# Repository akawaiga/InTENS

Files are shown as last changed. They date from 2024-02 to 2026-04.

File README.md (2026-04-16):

# InTENS project

# Overview
The InTENS is a high-frequency and high-intensity nerve stimulation
treatment for pain management. This project builds on prior research
from Boston Univesity's EDF and Bridge BUilders program, guided by a
physician, and is supplemented by phantom model testing and a new
electrode design.

# Features
*   single-channel system for compactness
*   delivers sine waves instead of commercial TENS pulse for user comfort
*   capable of delivering frequecnies up of atleast 1kHz
*   capable of delivering high-intensity waves of up to 140 Vpp

# Changes required to the board before use:

*   Solder a wire between pins 1 and 6 of U1 (best done on the bottom side)
This connects DAC reference to 5V
*   Solder a wire between J4 pin 3 and J2 pin 5
*   Solder a wire between J4 pin 4 and J2 pin 7
This connects the SPI data and clock to the right Arduino pins
*   addd a 100kohm resistor to R5 as 2mA is the reccommended ouptut current (for saftey)(ArduinoSheild PCB) 
*   addd a 100kohm resistor to C4 and C6 to reduce load on DC DC conversrters so both can function at same time (Battery PCB) 
*   heat sink reccommended on the 5V regulator (U1 on BatteryPCB) 

# User Interface 
Installation of Arduino IDE and Packages

* IDE download - https://www.arduino.cc/en/software
* Pathway to DAC MCP Package - https://github.com/akawaiga/InTENS/tree/main/Arduino 

Setup

*  Start Arduino IDE and connect the InTens device to the laptop. Ensure the correct board and output port are selected within the IDE. 
*  Ensure the DAC MCP library is downloaded from the GitHub repository
*  Set output baud rate to 11500
*  Upload the code to the Arduino and turn on both switches

Controlling Frequency and Amplitude

*   The initial frequency can be set using the freq variable. 
*   The initial amplitude can be set using the desiredAmplitude variable. 
*   The increment for the frequency can be set by changing the integer
  value in code line “freq+=10” and “freq-=10”.
*   The increment for the amplitude can be set by changing the integer
  value in code line “desiredAmplitude+=10” and
  “desiredAmplitude-=10”.
*   The frequency can be increased by entering “+” in the Arduino IDE.
*   The frequency can be decreased by entering “-” in the Arduino IDE.
*   The amplitude can be increased by entering “A” in the Arduino IDE. 
*   The amplitude can be decreased by entering “a” in the Arduino IDE. 

Note: 

You can compound your increments by adding multiple inputs at
once. For example: “+++++” or “AAAA”. Avoid combining inputs such as
“AaA”.

The code currently does not support decimal point increments (float),
please use integers such as “1” or “25”.

# Conclusion
Though with 2 PCBs we have acheived the orginal goal of creating a
TENS device capcable of creating a sine wave, >1kHz frequecny, and
140Vpp amplitude, we recommend the following updates to the next
iteration of the device:

*   Shaft Encoder:incorporate a knob to manually control frequency and
  amplitude rather than through the IDE. This has been done in
  previous versions of the device (2021-22)
*   LCD Display:incorporate LCD display to show output frequency and
  amplitude and various parameter changes when changing parameters
  using the knob.
*   Float type increments: currently the code uses type int for the
  amplitude and frequency variables, update this to type float to
  allow decimal increments.
*   Safety: consult with electrical engineers to build in further safety
  features to ensure the device does not provide unwanted currents to
  the patient.
*   Finger Clamp: update the finger clamp design to include jaws
  (example a claw hair clip) so it can accommodate smaller patient
  anatomies.
*   Phantom Testing: continue developing a phantom model for the finger
  to demonstrate safety and efficacy.

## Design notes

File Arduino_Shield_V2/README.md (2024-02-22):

# Design review 2/22/24

**Schematic / Overall**

* Why the change to the TSSOP package for the LTC6090?.  The SO-8
  package is much easier to solder and in stock.
* Missing HV power supplies on the LTC6090.  You need to be able to
  supply external power to this for testing at voltages above 5V.
  Suggest to add a 3 pin connector with +HV, GND, -HV which are
  connected to the V+, GND, V- on the LTC6090
* The chips are missing bypass capacitors.  Please read over the
  datahsheets for recommendations.  These are capacitors to GND on
  each power supply to a chip (so total of 3 minimum, Vdd the MCP4921
  and two on V+ and V- of the LTC6090)  
* Mounting holes should be on schematic
* Name symbols consistently:  you have U1 and IC1 where you should
  have U1 and U2.
* Don't interconnect the two SDA and SCL pins on the Arduino.

**PCB Layout**

The layout looks nice and neat, but there are quite a few issues which
should be addressed to ensure good performance:

* There must be an overall GND plane.  This is most easily done by
  converting the design to 4 layers and using an inner layer for this.
* The bypass capacitors mentioned above need to be placed near the
  chips.
* The datasheet for the LTC6090 (did you read it?) specifically
  reccomends surface-mount components.  I highly recommend switching
  all the passives (R, C) to surface mount.  An 0805 or 1206 size is
  quite large and easy to use.  I can help you with soldering them.

The wiring seems a bit random... did you use the autoroute feature?
Never do that.

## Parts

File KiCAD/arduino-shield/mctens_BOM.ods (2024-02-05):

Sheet: mctens
Please order for two boards plus 1 spare of each IC and round up on the passives.
Reference | Qty/Board | Value | Footprint | CatNo | Vendor | QQ | Project
BT1 BT2 | 2 | Battery_Holder |  | 36-2478-ND | DigiKey |  | MULTI-TEMS
C3 | 1 | 1uF | Capacitor_THT:C_Disc_D3.4mm_W2.1mm_P2.50mm | 399-14394-1-ND | DigiKey |  | MULTI-TEMS
C1 C2 C4 C5 C6 C11 | 6 | 0.1uF | Capacitor_THT:C_Disc_D3.4mm_W2.1mm_P2.50mm | 399-9859-2-ND | DigiKey |  | MULTI-TEMS
C7 C8 C9 C10 | 4 | OMIT | Capacitor_THT:C_Disc_D3.4mm_W2.1mm_P2.50mm | OMIT
D1 D2 D3 D4 | 4 | 1N4005 | Diode_THT:D_DO-41_SOD81_P10.16mm_Horizontal | 1N4007-TPMSCT-ND | DigiKey |  | MULTI-TEMS
D5 D6 | 2 | LED | LED_THT:LED_D3.0mm | 1497-XLMDK65D-ND | DigiKey |  | MULTI-TEMS
H1 H2 H3 H4 | 4 | MountingHole | MountingHole:MountingHole_4.3mm_M4 | OMIT
J1 | 1 | Conn_01x02 | Connector_Molex:Molex_Mini-Fit_Jr_5566-02A_2x01_P4.20mm_Vertical | WM23820-ND | DigiKey |  | MULTI-TEMS
J2 J3 J4 J5 | 4 | CONN | Connector_PinHeader_2.54mm:PinHeader_1x02_P2.54mm_Vertical | S1011EC-02-ND | DigiKey |  | MULTI-TEMS
J6 | 1 | Conn_01x16 | Connector_PinHeader_2.54mm:PinHeader_1x16_P2.54mm_Vertical | 2057-PH1-16-UA-ND | DigiKey |  | MULTI-TEMS
N1 | 1 | Enclosure_1591DSBK |  | HM105-ND | DigiKey |  | MULTI-TEMS
Q1 Q2 Q3 Q4 | 4 | FQP19N20C | Package_TO_SOT_THT:TO-220-3_Vertical | FQP19N20C-ND | DigiKey |  | MULTI-TEMS
R12 | 1 | 1k | Resistor_THT:R_Axial_DIN0207_L6.3mm_D2.5mm_P10.16mm_Horizontal | Generic 1k ohm 1/4W | DigiKey |  | MULTI-TEMS
R10 R13 R14 R15 | 4 | 10k | Resistor_THT:R_Axial_DIN0207_L6.3mm_D2.5mm_P10.16mm_Horizontal | Generic 10k ohm 1/4W | DigiKey |  | MULTI-TEMS
R11 R16 R17 | 3 | 2k | Resistor_THT:R_Axial_DIN0207_L6.3mm_D2.5mm_P10.16mm_Horizontal | Generic 2k ohm 1/4W | DigiKey |  | MULTI-TEMS
R1 R2 R3 R6 R7 | 5 | 100 | Resistor_THT:R_Axial_DIN0207_L6.3mm_D2.5mm_P10.16mm_Horizontal | Generic 100 ohm 1/4W | DigiKey |  | MULTI-TEMS
R4 R5 R8 R9 | 4 | 8R2 2W | Resistor_THT:R_Axial_DIN0414_L11.9mm_D4.5mm_P20.32mm_Horizontal | 8.2 ohm 2W | DigiKey |  | MULTI-TEMS
RV1 | 1 | 5K | Potentiometer_THT:Potentiometer_Bourns_3266P_Horizontal | 3266P-1-502LF-ND | DigiKey |  | MULTI-TEMS
SW1 | 1 | SW_SPST | arduino-shield:SW-A11AB | 360-3868-ND | DigiKey |  | MULTI-TEMS
SW2 | 1 | COM-15140 | arduino-shield:rotary-RG | OMIT
T1 T2 T3 T4 | 4 | Transformer_1P_1S | arduino-shield:42TL-transformer | OMIT - customer
U2 | 1 | 12V_3.3V_DC | Package_TO_SOT_THT:TO-220-3_Vertical | 1951-TSR1.5-2433E-ND | DigiKey |  | MULTI-TEMS
U3 | 1 | LM358 | Package_DIP:DIP-8_W7.62mm_Socket_LongPads | LM2904NNS/NOPB-ND | DigiKey |  | MULTI-TEMS
U4 | 1 | MAX4678 | Package_DIP:DIP-16_W7.62mm_Socket_LongPads | MAX4678EPE+-ND | DigiKey |  | MULTI-TEMS
U5 | 1 | ARDUINO_PRO_MINI | arduino-shield:MODULE_ARDUINO_PRO_MINI
XX1 | 4 | 2 Pin Housing |  | WM2800 | DigiKey | 4 | MULTI-TEMS
XX2 | 8 | Crimp Pins |  | WM2513 | DigiKey | 8 | MULTI-TEMS
XX3 | 4 | 3.5 mm jack |  | 839-1410-ND | DigiKey | 4 | MULTI-TEMS
XX4 | 4 | 3.5 mm cable |  | 839-1033-ND | DigiKey | 4 | MULTI-TEMS
XX5 | 4 | 16 pin socket |  | 929850-01-16-ND | DigiKey | 4 | MULTI-TEMS

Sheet: EDF stock
Qty
20 | Breakaway header | 3M11928-ND | DigiKey | EDF Stock
20 | Breakaway socket | 929850-01-36-ND | DigiKey | EDF Stock
10 | Breakaway header long pins | SAM1123-32-ND | DigiKey | EDF Stock
10 | Breakaway header two row | S2011EC-40-ND | DigiKey | EDF Stock

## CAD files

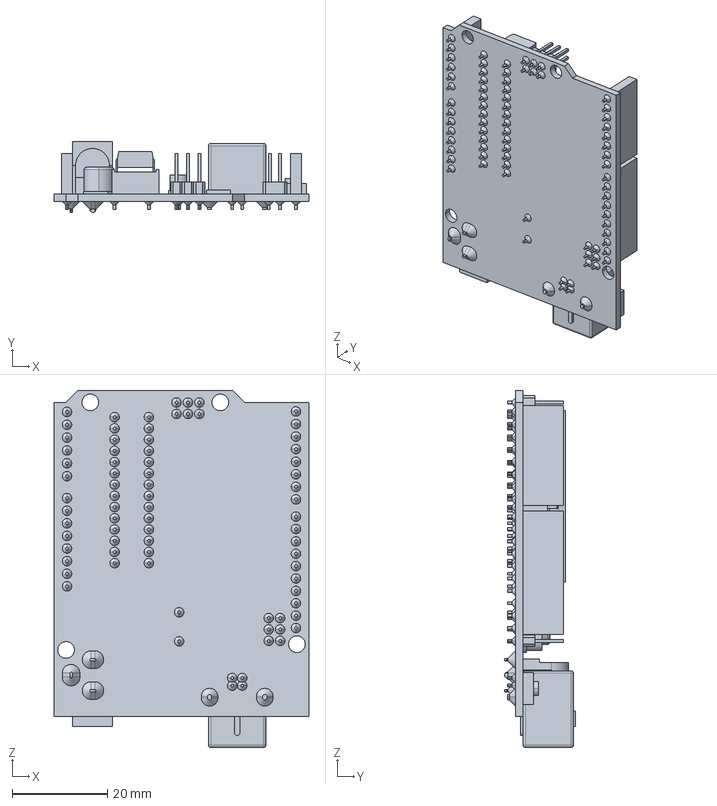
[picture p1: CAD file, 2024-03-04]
Arduino_Shield_V2/Arduino-UNO.stp
53.5 x 14.9 x 75.0 mm

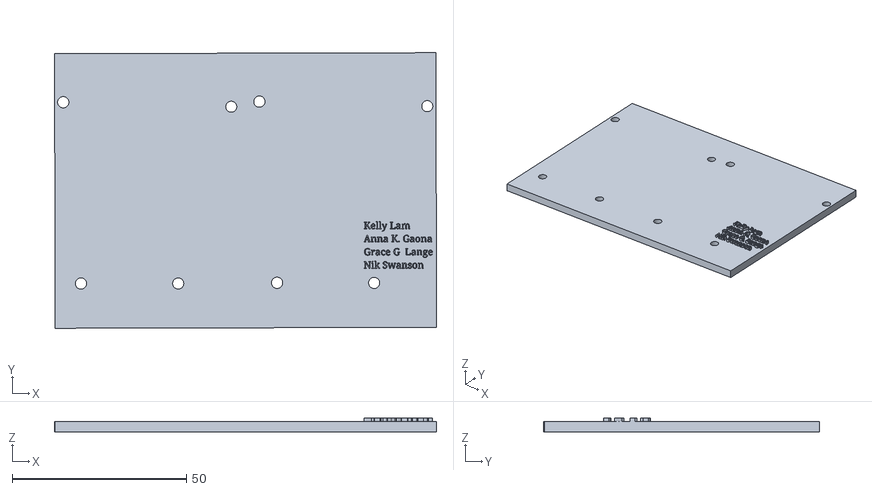
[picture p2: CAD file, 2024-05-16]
CAD Designs/layer.stl
109.8 x 79.2 x 4.00

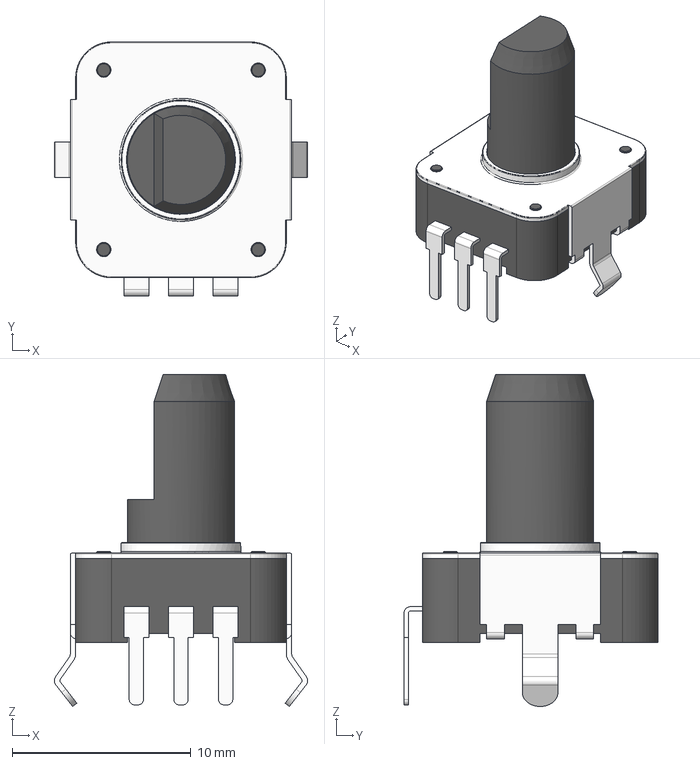
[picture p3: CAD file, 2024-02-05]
KiCAD/arduino-shield/3D/EC12 Encoder 10mm 3pin.stp
14.2 x 14.2 x 18.6 mm

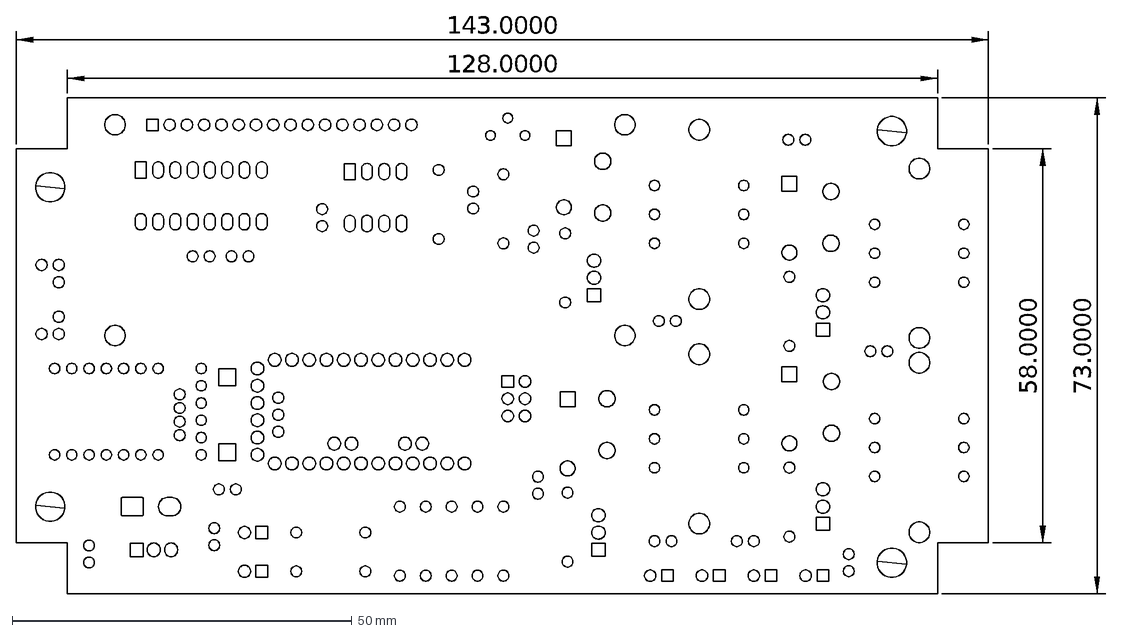
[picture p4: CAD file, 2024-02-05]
KiCAD/arduino-shield/DXF/mctens-Edge_Cuts.dxf
128.0000
143.0000
58.0000
73.0000

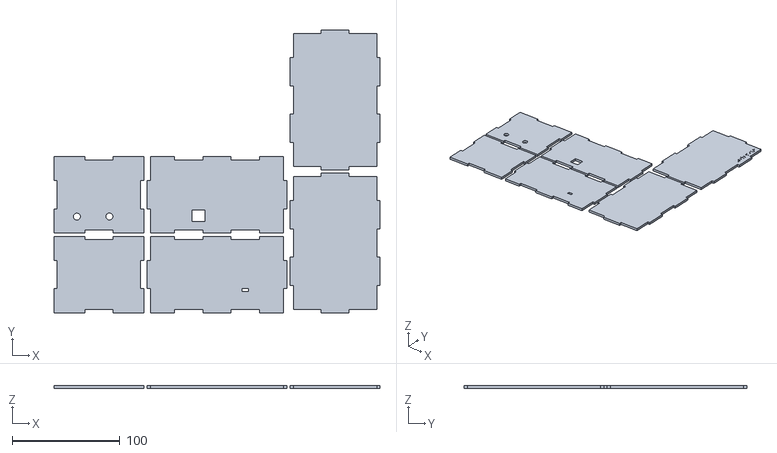
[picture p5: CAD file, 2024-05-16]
CAD Designs/makercase.stl
302.7 x 262.4 x 3.20

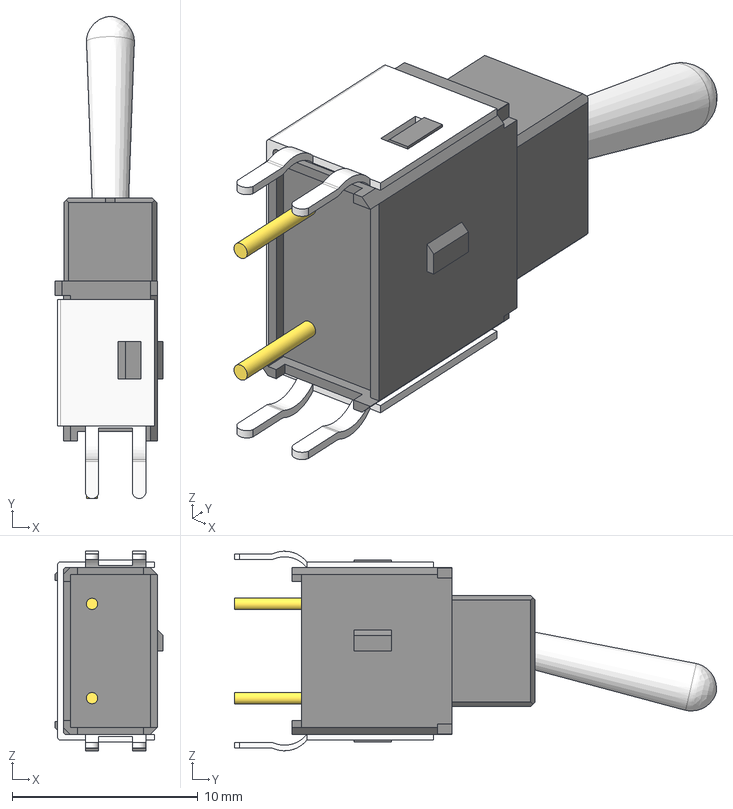
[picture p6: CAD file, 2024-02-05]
KiCAD/arduino-shield/3D/A11AB.stp
5.84 x 26.0 x 10.8 mm
_A1-toggle-body
_A11B-toggle-terminals
_A1B-toggle-bracket_str
_AA-toggle-toggle

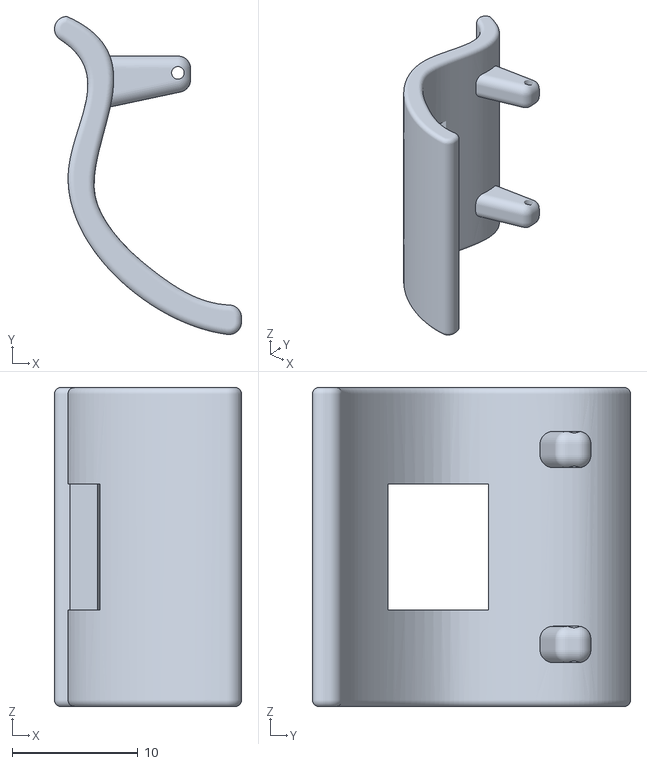
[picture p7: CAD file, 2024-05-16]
CAD Designs/halfclamplargedistance.STL
14.9 x 25.3 x 25.4

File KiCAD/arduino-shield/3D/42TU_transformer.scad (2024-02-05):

// 42TU transformer

dy = .1675;
dx = .517;

cx = 0.72;
cy = 0.98;
cz = 0.74;

module trans() {
  // body
  color("grey")
    translate( [cx/3, 0, 0])
      cube( [cx/3, cy, cz]);
  color("#e0e0e0") {
      translate( [0, cy/5, cz/8])  cube( [cx, cy*3/5, 0.063]);
      translate( [0, cy/5, cz*6/8])  cube( [cx, cy*3/5, 0.063]);
  }
  color("#ffffe0") {
    translate( [cx/8, cy/5, cz/8])  cube( [cx*3/4, cy*3/5, cz*5/8]);
  }

  // wires
  translate( [0.1, 0.323, -.197]) {
    for( ix=[0:1]) {
      for( iy=[0:2]) {
	translate( [ix*dx, iy*dy, 0])
	  cylinder( d=.02, h=.3);
      }
    }
  }

  // tabs
  color("#e0e0e0") {
    translate( [cx/2-.05, 0, -0.2])
      cube( [.1, .03, .2]);
    translate( [cx/2-.05, cy-.03, -0.2])
      cube( [.1, .03, .2]);
  }
}

trans();

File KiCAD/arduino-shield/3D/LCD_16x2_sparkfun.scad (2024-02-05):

module lcd() {

  // PCB with mounting holes
  difference() {
    color("#006020")  cube([80,36,1.6]);
    translate( [0, 0, -0.1]) {
      $fn = 24;
      translate( [2.5, 2.5, 0])  cylinder( d=2.5, h=1.8);
      translate( [2.5, 36-2.5, 0])  cylinder( d=2.5, h=1.8);
      translate( [80-2.5, 2.5, 0])  cylinder( d=2.5, h=1.8);
      translate( [80-2.5, 36-2.5, 0])  cylinder( d=2.5, h=1.8);
    }
  }
  // display body
  translate([4.35, 4.85, 3.2]) color("grey") cube([71.3, 26.3, 5.4]);
  // connector pins
  color("#FFFF00")
  translate( [8, 36-2.5, -5]) {
    $fn = 4;
    for( i=[0:15]) {
      translate( [i*2.54, 0, 0])
	cylinder( d=1.0,h=7);
    }
  }
}

lcd();


    

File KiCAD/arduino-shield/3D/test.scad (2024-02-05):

// PCB with mounting holes
difference() {
  color("#006020")  cube([80,36,1.6]);
  translate( [0, 0, -0.1]) {
    $fn = 24;
    translate( [2.5, 2.5, 0])  cylinder( d=2.5, h=1.8);
    translate( [2.5, 36-2.5, 0])  cylinder( d=2.5, h=1.8);
    translate( [80-2.5, 2.5, 0])  cylinder( d=2.5, h=1.8);
    translate( [80-2.5, 36-2.5, 0])  cylinder( d=2.5, h=1.8);
  }
}
// display body
translate([4.35, 4.85, 3.2]) color("grey") cube([71.3, 26.3, 5.4]);
// connector pins
translate( [8, 36-2.5, -5]) {
  for( i=[0:15]) {
    translate( [i*2.54, 0, 0])
    cylinder( d=1.0,h=7);
  }
}

    

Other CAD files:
KiCAD/arduino-shield/DXF/mctens-F_Mask.dxf

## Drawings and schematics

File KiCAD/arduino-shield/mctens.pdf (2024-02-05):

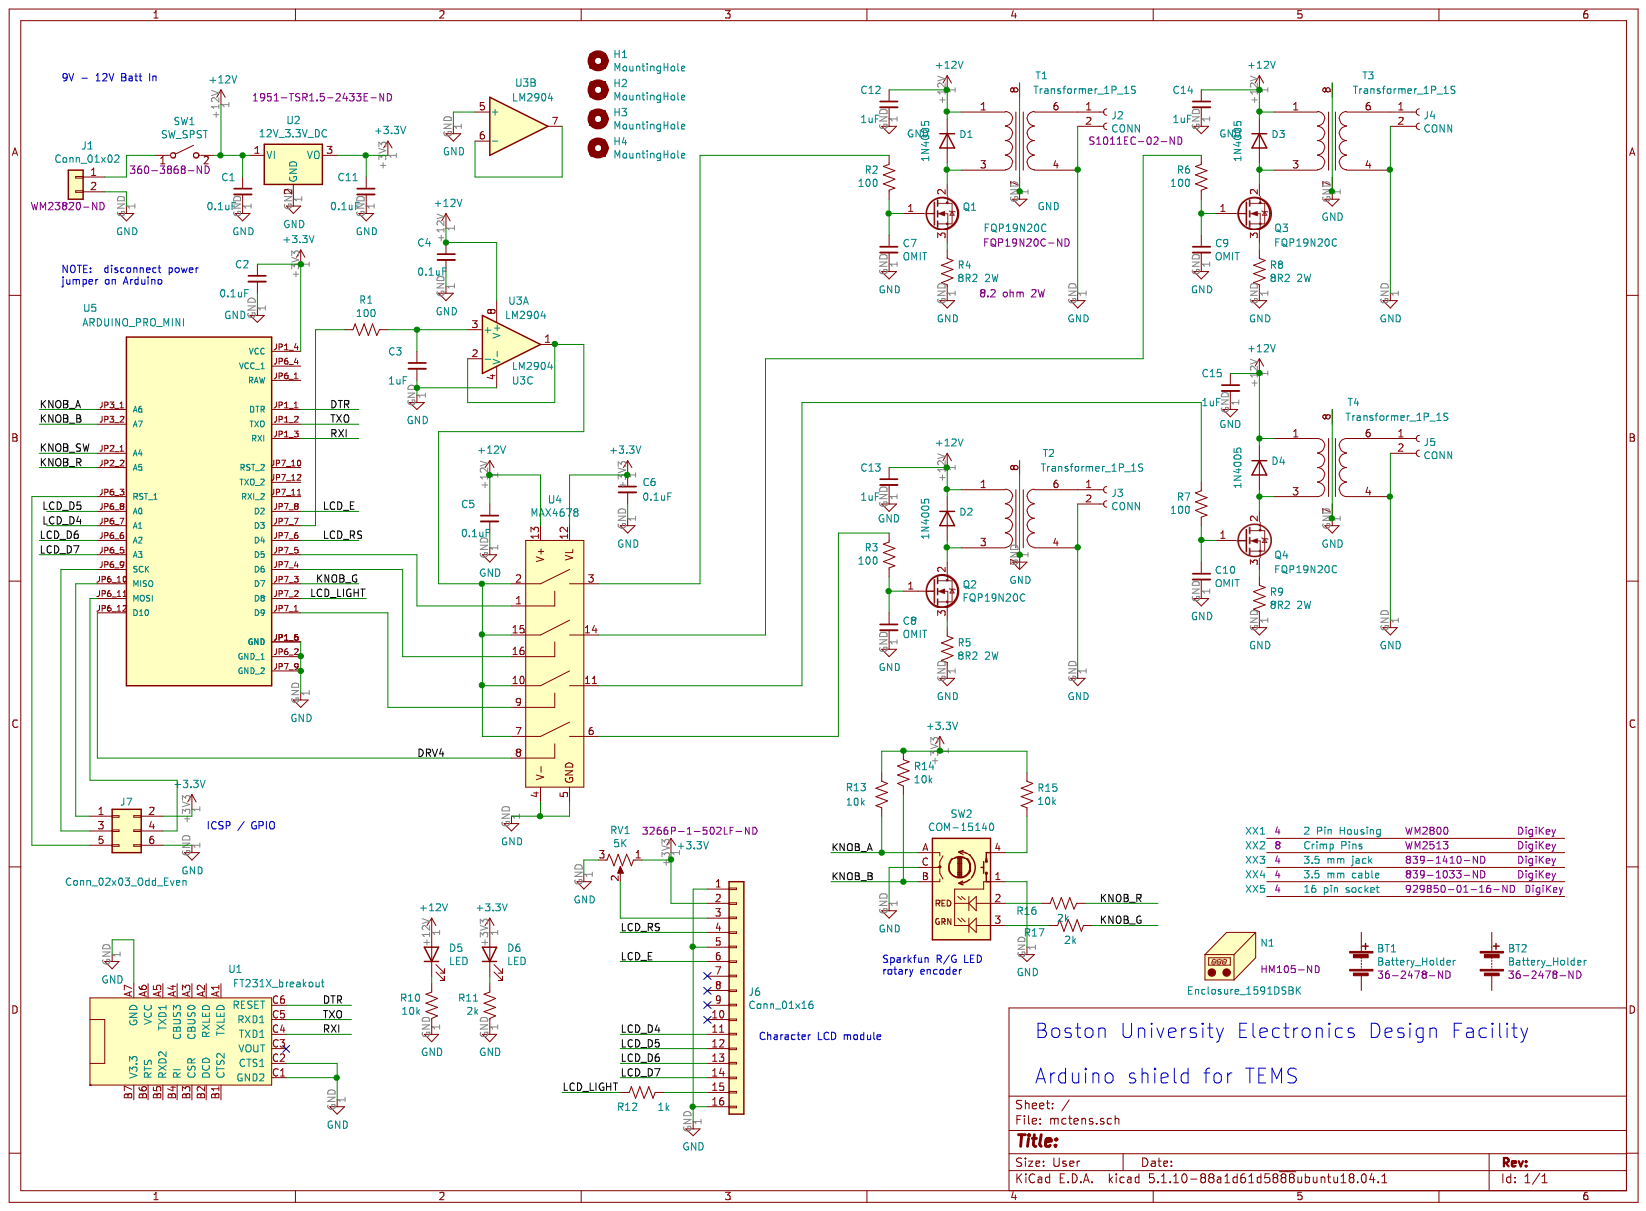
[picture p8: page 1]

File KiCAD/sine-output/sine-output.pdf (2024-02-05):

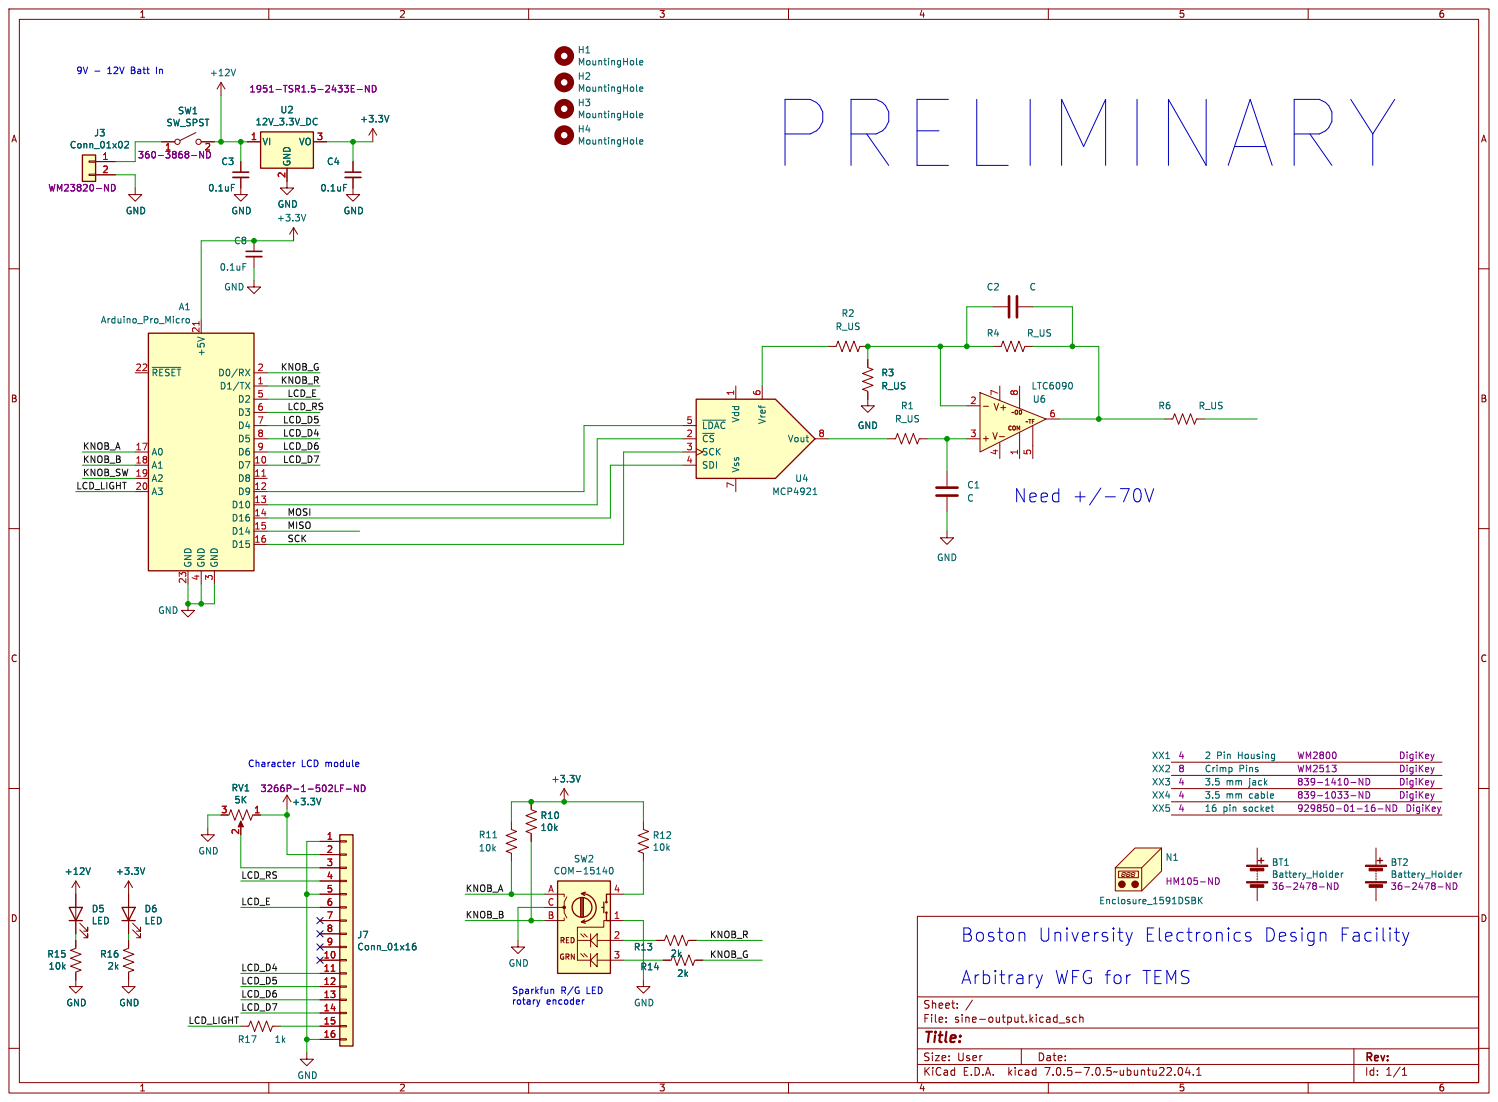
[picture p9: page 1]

1 ~{CS} 2 SCK 3 SDI 4 ~{LDAC} 5 Vref 6 Vss 7 Vout 8 U4 MCP4921 GND

Arbitrary WFG for TEMS

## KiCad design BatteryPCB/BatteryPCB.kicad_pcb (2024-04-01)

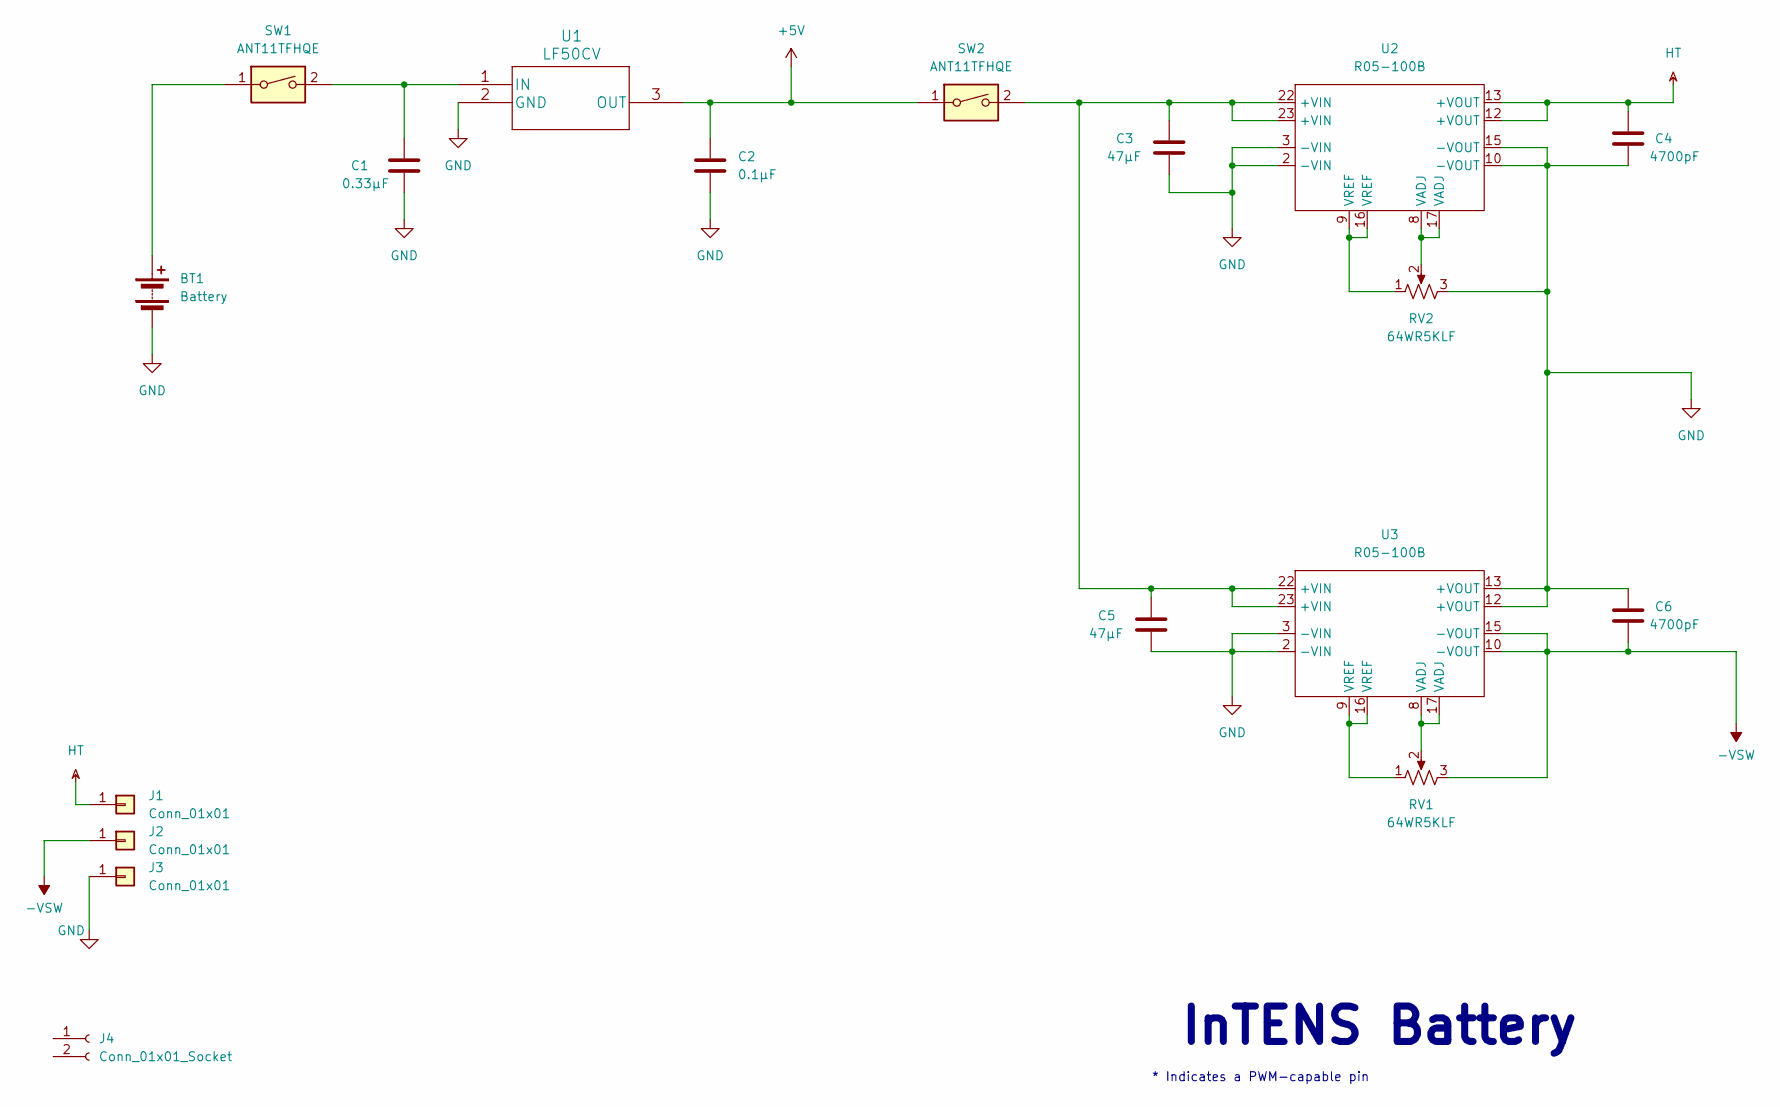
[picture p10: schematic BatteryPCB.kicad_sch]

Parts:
BT1: Battery; CON_39296028
C1: 0.33μF; C_Rect_L4.6mm_W2.0mm_P2.50mm_MKS02_FKP02
C2: 0.1μF; C_Rect_L4.6mm_W2.0mm_P2.50mm_MKS02_FKP02
C3, C5: 47μF; C_1206_3216Metric_Pad1.33x1.80mm_HandSolder
C4, C6: 4700pF; C_1206_3216Metric_Pad1.33x1.80mm_HandSolder
J1, J2, J3: Conn_01x01; Pin_D1.0mm_L10.0mm
J4: Conn_01x01_Socket; PinSocket_1x02_P2.54mm_Vertical
RV1, RV2: 64WR5KLF; RES3_64W_TTE
SW1, SW2: ANT11TFHQE; 100SP1T1_EWI
U1: LF50CV
U2, U3: R05-100B; DIP-24_W15.24mm

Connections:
+5V: C2.1, SW2.1, U1.3 (OUT)
-VSW: C6.1, J2.1, RV1.3, U3.10 (-VOUT), U3.15 (-VOUT)
GND: BT1.2 (-), C1.2, C2.2, C3.1, C4.1, C5.1, C6.2, J3.1, RV2.3, U1.2 (GND), U2.2 (-VIN), U2.3 (-VIN), U2.10 (-VOUT), U2.15 (-VOUT), U3.2 (-VIN), U3.3 (-VIN), U3.12 (+VOUT), U3.13 (+VOUT)
HT: C4.2, J1.1, U2.12 (+VOUT), U2.13 (+VOUT)
unnamed: BT1.1 (+), SW1.1
unnamed: C3.2, C5.2, SW2.2, U2.22 (+VIN), U2.23 (+VIN), U3.22 (+VIN), U3.23 (+VIN)
unnamed: RV1.1, U3.9 (VREF), U3.16 (VREF)
unnamed: RV1.2, U3.8 (VADJ), U3.17 (VADJ)
unnamed: RV2.1, U2.9 (VREF), U2.16 (VREF)
unnamed: RV2.2, U2.8 (VADJ), U2.17 (VADJ)
unnamed: C1.1, SW1.2, U1.1 (IN)

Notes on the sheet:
InTENS Battery
* Indicates a PWM-capable pin

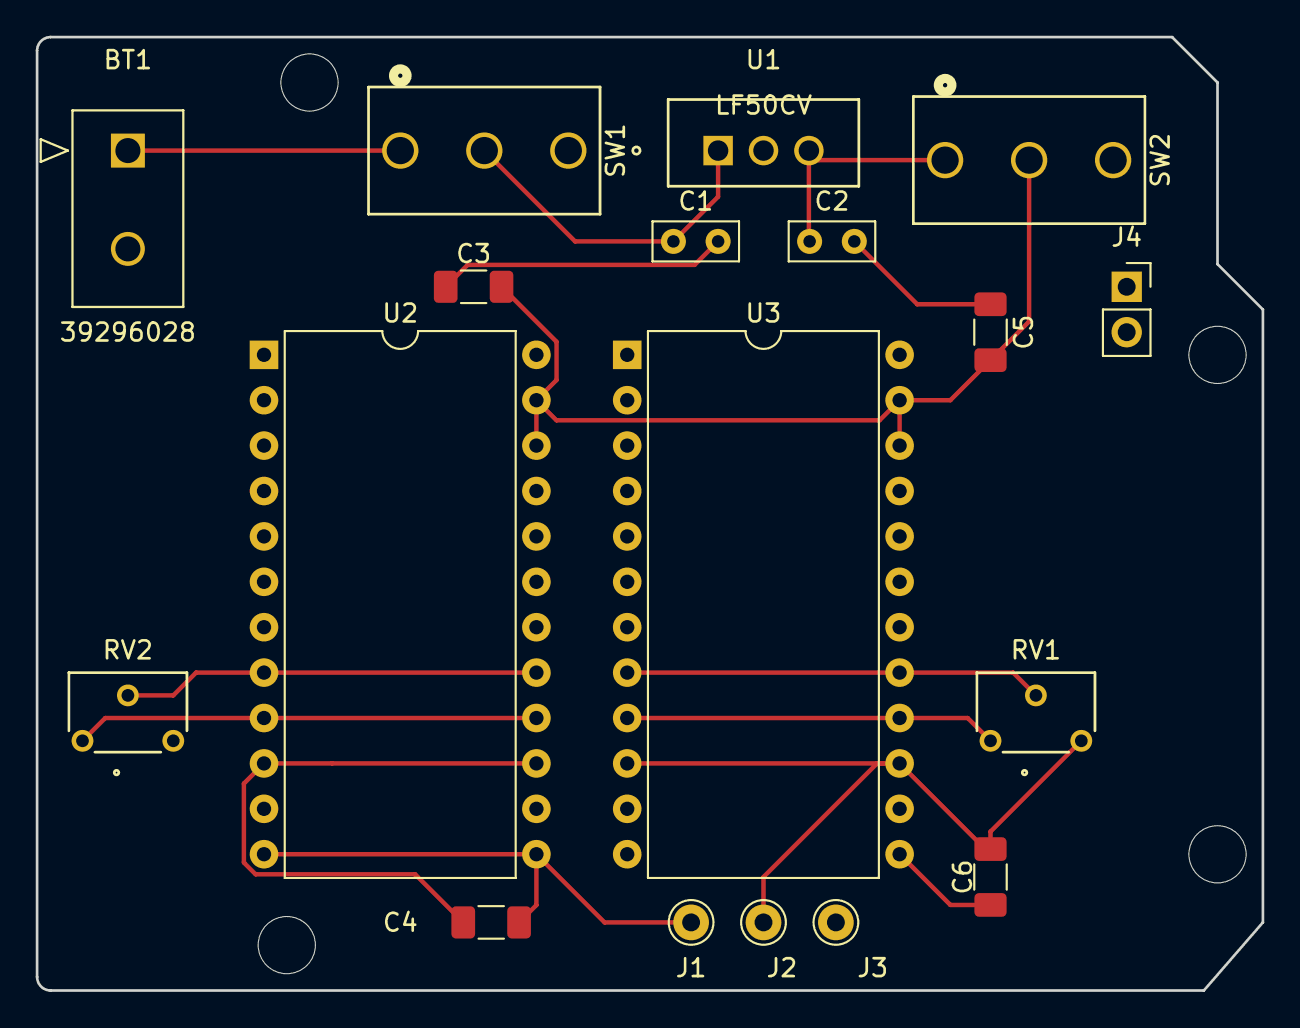
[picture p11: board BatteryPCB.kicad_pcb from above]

Board: 2 copper layers, 68.6 x 53.3 mm, 22 parts (0 on the bottom side), 11 nets.

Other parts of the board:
MH1, MH2, MH3, MH4: MountingHole_3.2mm

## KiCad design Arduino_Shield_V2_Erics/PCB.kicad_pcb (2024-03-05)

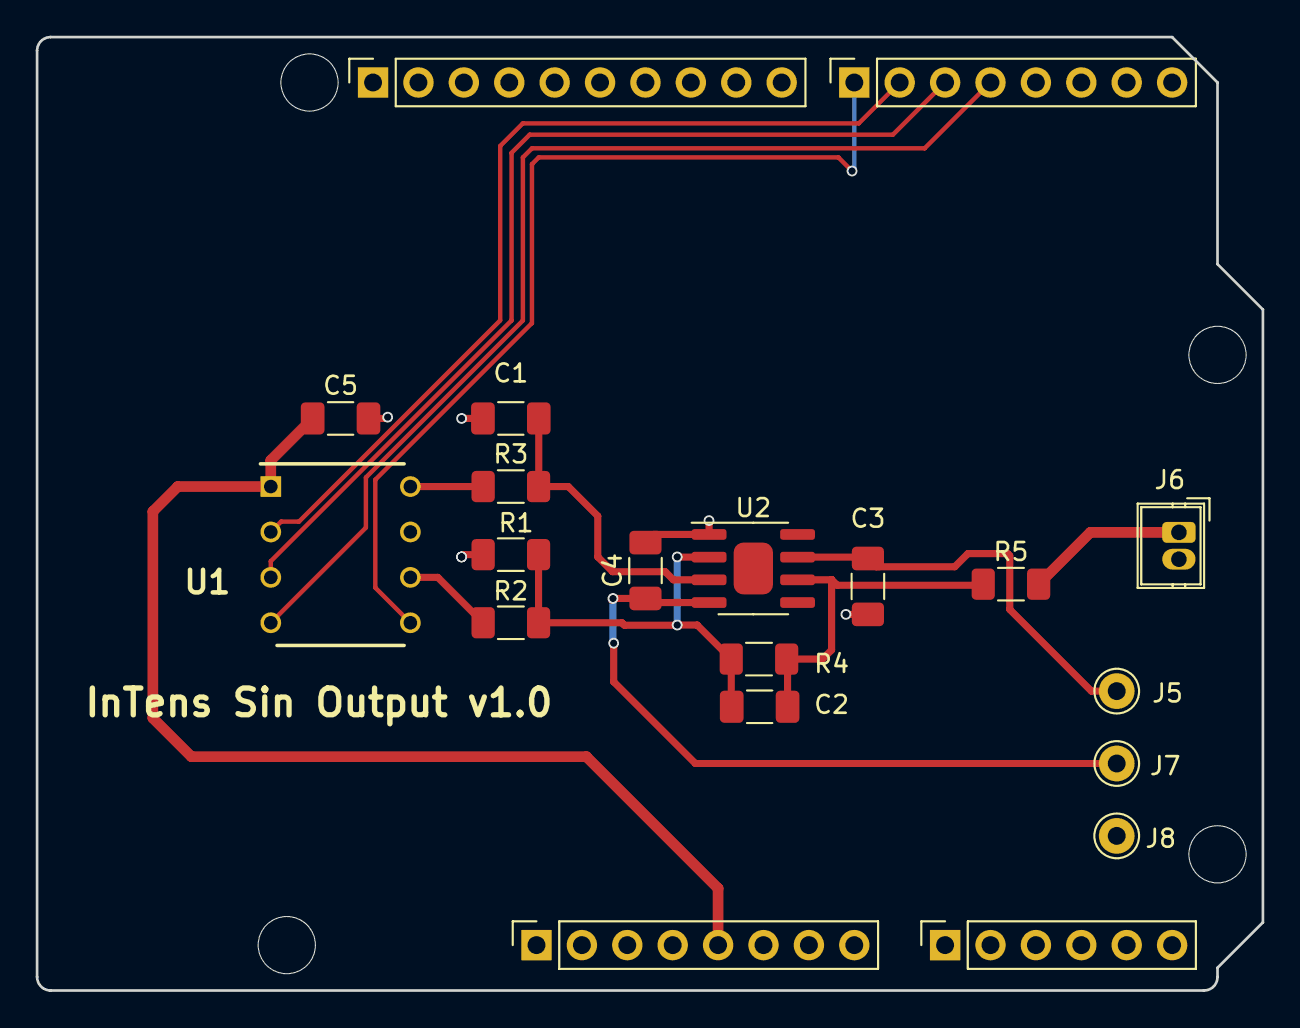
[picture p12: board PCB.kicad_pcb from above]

Board: 2 copper layers, 68.6 x 53.3 mm, 24 parts (0 on the bottom side), 15 nets.

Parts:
C1: 470pF; C_1206_3216Metric_Pad1.33x1.80mm_HandSolder
C2: 10pF; C_1206_3216Metric_Pad1.33x1.80mm_HandSolder
C3, C4: 0.1uF; C_1206_3216Metric_Pad1.33x1.80mm_HandSolder
C5: 0.1 uF; C_1206_3216Metric_Pad1.33x1.80mm_HandSolder
J1: Power; PinSocket_1x08_P2.54mm_Vertical
J2: Digital/PWM; PinSocket_1x10_P2.54mm_Vertical
J3: Analog; PinSocket_1x06_P2.54mm_Vertical
J4: Digital/PWM; PinSocket_1x08_P2.54mm_Vertical
J5, J7, J8: Conn_01x01; Pin_D1.0mm_L10.0mm
J6: Conn_01x01_Socket; Wuerth_WR-WTB_64800211622_1x02_P1.50mm_Vertical
MH1, MH2, MH3, MH4: MountingHole_3.2mm
R1: 16.2kΩ; R_1206_3216Metric_Pad1.30x1.75mm_HandSolder
R2: 16.9kΩ; R_1206_3216Metric_Pad1.30x1.75mm_HandSolder
R3: 10kΩ; R_1206_3216Metric_Pad1.30x1.75mm_HandSolder
R4: 453kΩ; R_1206_3216Metric_Pad1.30x1.75mm_HandSolder
R5: 40kΩ; R_1206_3216Metric_Pad1.30x1.75mm_HandSolder
U1: MCP4921; DIP781W56P254L950H533Q8N
U2: LTC6090; SOIC-8-1EP_3.9x4.9mm_P1.27mm_EP2.29x3mm

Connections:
+5V: C5.1, J1.5, U1.1 (Vdd)
-VSW: C4.1, J7.1, U2.4
/4: J4.4, U1.4 (SDI)
/7: J4.1, U1.5 (~LDAC)
/*5: J4.3, U1.3 (SCK)
/*6: J4.2, U1.2 (~CS)
GND: C1.2, C3.2, C4.2, C5.2, J1.6, J1.7, J2.4, J6.2, J8.1, R2.1, U1.7 (Vss), U2.1
HT: C3.1, J5.1, U2.7
unnamed: C1.1, R3.2, U2.3
unnamed: C2.1, R1.1, R2.2, R4.1, U2.2
unnamed: C2.2, R4.2, R5.1, U2.6
unnamed: J6.1, R5.2
unnamed: R3.1, U1.8 (Vout)
unnamed: R1.2, U1.6 (Vref)
unnamed: U2.5, U2.8

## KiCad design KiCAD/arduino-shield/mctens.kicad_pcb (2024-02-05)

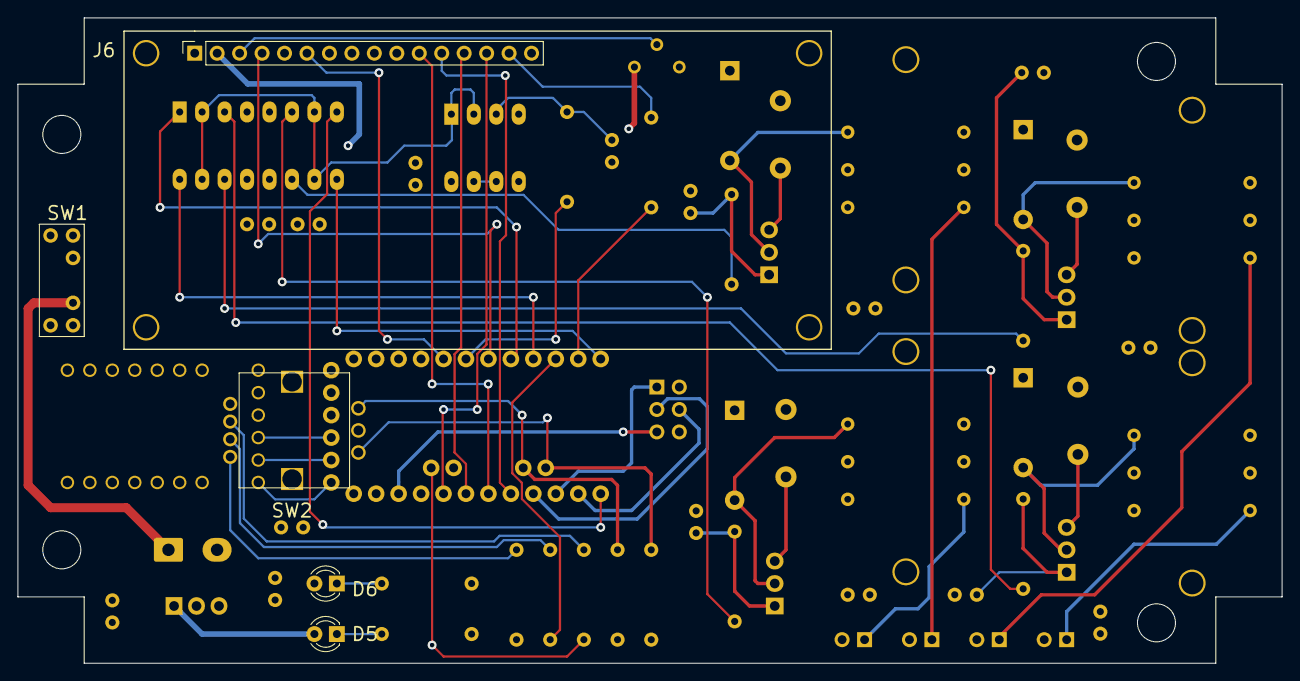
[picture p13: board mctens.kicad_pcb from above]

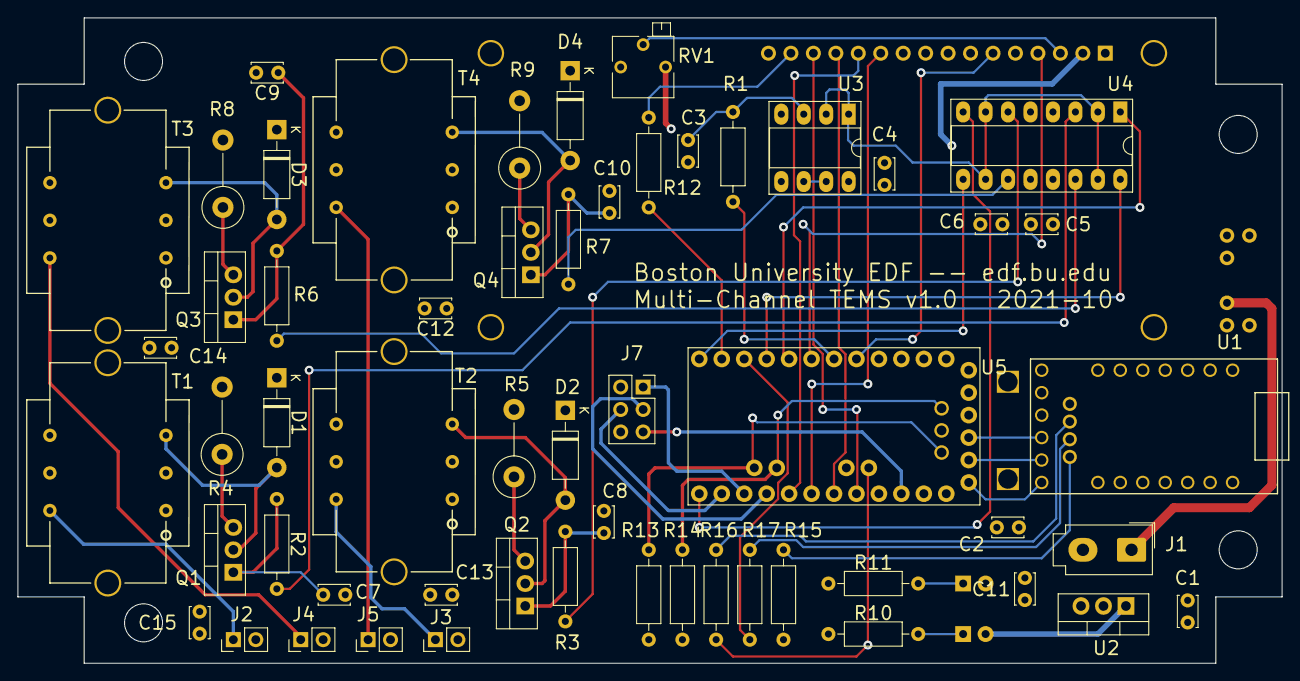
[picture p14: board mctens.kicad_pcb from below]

Board: 4 copper layers, 143.0 x 73.0 mm, 65 parts (56 on the bottom side), 57 nets.

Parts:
C1, C2, C4, C5, C6, C11: 0.1uF; C_Disc_D3.4mm_W2.1mm_P2.50mm
C3, C12, C13, C14, C15: 1uF; C_Disc_D3.4mm_W2.1mm_P2.50mm
C7, C8, C9, C10: OMIT; C_Disc_D3.4mm_W2.1mm_P2.50mm
D1, D2, D3, D4: 1N4005; D_DO-41_SOD81_P10.16mm_Horizontal
D5, D6: LED; LED_D3.0mm
H1, H2, H3, H4: MountingHole; MountingHole_4.3mm_M4
J1: Conn_01x02; Molex_Mini-Fit_Jr_5566-02A_2x01_P4.20mm_Vertical
J2, J3, J4, J5: CONN; PinHeader_1x02_P2.54mm_Vertical
J6: Conn_01x16; LCD_module_3D
J7: Conn_02x03_Odd_Even; PinSocket_2x03_P2.54mm_Vertical
Q1, Q2, Q3, Q4: FQP19N20C; TO-220-3_Vertical
R1, R2, R3, R6, R7: 100; R_Axial_DIN0207_L6.3mm_D2.5mm_P10.16mm_Horizontal
R4, R5, R8, R9: 8R2 2W; R_Axial_DIN0414_L11.9mm_D4.5mm_P7.62mm_Vertical
R10, R13, R14, R15: 10k; R_Axial_DIN0207_L6.3mm_D2.5mm_P10.16mm_Horizontal
R11, R16, R17: 2k; R_Axial_DIN0207_L6.3mm_D2.5mm_P10.16mm_Horizontal
R12: 1k; R_Axial_DIN0207_L6.3mm_D2.5mm_P10.16mm_Horizontal
RV1: 5K; Potentiometer_Bourns_3266P_Horizontal
SW1: SW_SPST; SW-A11AB-3D
SW2: COM-15140; rotary-RG-3D
T1, T2, T3, T4: Transformer_1P_1S; 42TL-transformer-v2
U1: FT231X_breakout
U2: 12V_3.3V_DC; TO-220-3_Vertical
U3: LM358; DIP-8_W7.62mm_Socket_LongPads
U4: MAX4678; DIP-16_W7.62mm_Socket_LongPads
U5: ARDUINO_PRO_MINI; MODULE_ARDUINO_PRO_MINI_3D

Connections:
+3V3: C2.1, C6.1, C11.1, D6.2, J6.2, J7.2, R13.1, R14.1, R15.1, RV1.1, U2.3, U4.12, U5.JP1_4
+12V: C1.1, C4.1, C5.1, C12.1, C13.1, C14.1, C15.1, D1.1, D2.1, D3.1, D4.1, D5.2, SW1.2, T1.1, T2.1, T3.1, T4.1, U2.1, U3.8, U4.13
/DRV4: U4.8, U5.JP6_12
/DTR: U1.C6, U5.JP1_1
/KNOB_A: R13.2, SW2.A, U5.JP3_1
/KNOB_B: R14.2, SW2.B, U5.JP3_2
/KNOB_G: R17.1, U5.JP7_3
/KNOB_R: R16.1, U5.JP2_2
/LCD_D4: J6.11, U5.JP6_7
/LCD_D5: J6.12, U5.JP6_8
/LCD_D6: J6.13, U5.JP6_6
/LCD_D7: J6.14, U5.JP6_5
/LCD_E: J6.6, U5.JP7_8
/LCD_LIGHT: R12.2, U5.JP7_2
/LCD_RS: J6.4, U5.JP7_6
/RXI: U1.C4, U5.JP1_3
/TXO: U1.C5, U5.JP1_2
GND: C1.2, C2.2, C3.2, C4.2, C5.2, C6.2, C7.2, C8.2, C9.2, C10.2, C11.2, C12.2, C13.2, C14.2, C15.2, J1.2, J2.2, J3.2, J4.2, J5.2, J6.1, J6.5, J6.16, J7.6, R4.2, R5.2, R8.2, R9.2, R10.1, R11.1, RV1.3, SW2.1, SW2.C, T1.4, T1.7, T1.8, T2.4, T2.7, T2.8, T3.4, T3.7, T3.8, T4.4, T4.7, T4.8, U1.A7, U1.C1, U1.C2, U2.2, U3.4, U3.5, U4.4, U4.5, U5.JP1_5, U5.JP1_6, U5.JP6_2, U5.JP7_9
unnamed: C3.1, R1.1, U3.3
unnamed: C7.1, Q1.1, R2.1
unnamed: C8.1, Q2.1, R3.1
unnamed: C9.1, Q3.1, R6.1
unnamed: C10.1, Q4.1, R7.1
unnamed: D1.2, Q1.2, T1.3
unnamed: D2.2, Q2.2, T2.3
unnamed: D3.2, Q3.2, T3.3
unnamed: D4.2, Q4.2, T4.3
unnamed: D5.1, R10.2
unnamed: D6.1, R11.2
unnamed: J1.1, SW1.1
unnamed: J2.1, T1.6
unnamed: J3.1, T2.6
unnamed: J4.1, T3.6
unnamed: J5.1, T4.6
unnamed: J6.3, RV1.2
unnamed: J6.15, R12.1
unnamed: J7.1, U5.JP6_10
unnamed: J7.3, U5.JP6_9
unnamed: J7.4, U5.JP6_11
unnamed: J7.5, U5.JP6_3
unnamed: Q1.3, R4.1
unnamed: Q2.3, R5.1
unnamed: Q3.3, R8.1
unnamed: Q4.3, R9.1
unnamed: R1.2, U5.JP7_7
unnamed: R2.2, U4.3
unnamed: R3.2, U4.6
unnamed: R6.2, U4.14
unnamed: R7.2, U4.11
unnamed: R15.2, SW2.4
unnamed: R16.2, SW2.2
unnamed: R17.2, SW2.3
unnamed: U3.1, U3.2, U4.2, U4.7, U4.10, U4.15
unnamed: U3.6, U3.7
unnamed: U4.1, U5.JP7_5
unnamed: U4.9, U5.JP7_1
unnamed: U4.16, U5.JP7_4

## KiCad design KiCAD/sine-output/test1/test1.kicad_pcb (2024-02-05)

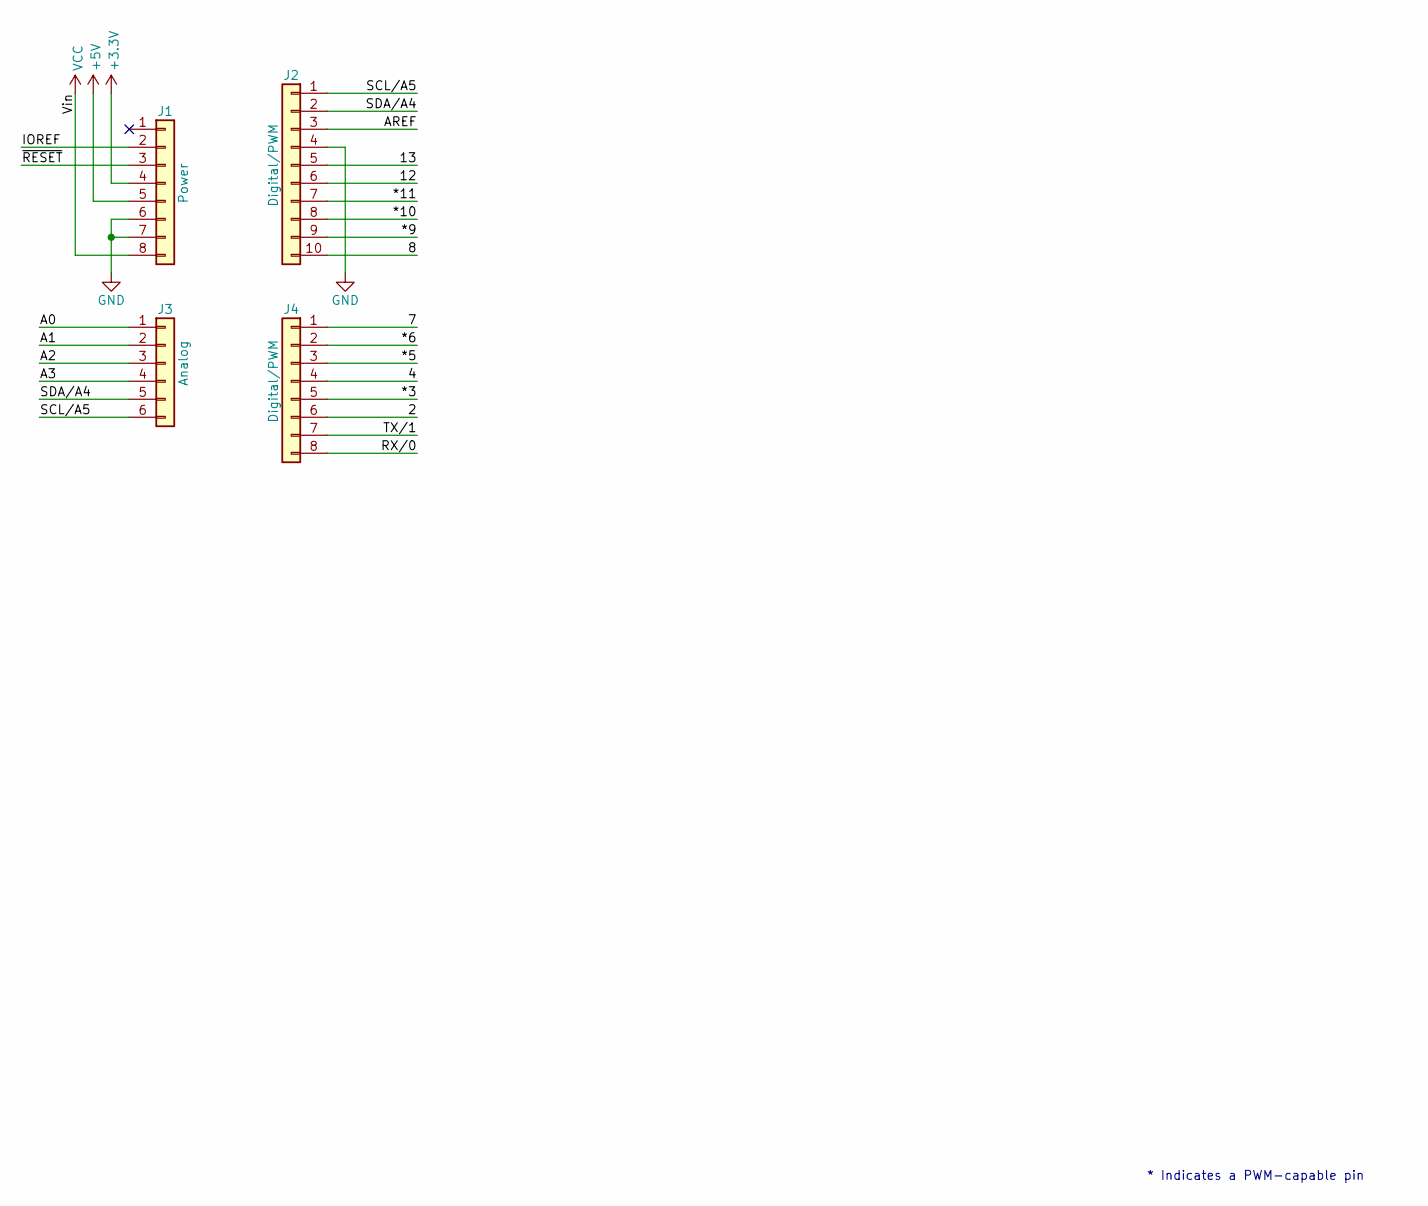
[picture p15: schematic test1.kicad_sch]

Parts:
J1: Power; PinSocket_1x08_P2.54mm_Vertical
J2: Digital/PWM; PinSocket_1x10_P2.54mm_Vertical
J3: Analog; PinSocket_1x06_P2.54mm_Vertical
J4: Digital/PWM; PinSocket_1x08_P2.54mm_Vertical

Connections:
+3V3: J1.4
+5V: J1.5
/2: J4.6
/4: J4.4
/7: J4.1
/8: J2.10
/12: J2.6
/13: J2.5
/*3: J4.5
/*5: J4.3
/*6: J4.2
/*9: J2.9
/*10: J2.8
/*11: J2.7
/A0: J3.1
/A1: J3.2
/A2: J3.3
/A3: J3.4
/AREF: J2.3
/IOREF: J1.2
/RX/0: J4.8
/SCL/A5: J2.1, J3.6
/SDA/A4: J2.2, J3.5
/TX/1: J4.7
/~RESET: J1.3
GND: J1.6, J1.7, J2.4
VCC: J1.8

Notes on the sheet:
* Indicates a PWM-capable pin

Board: 2 copper layers, 8 parts (0 on the bottom side), 3 nets, no tracks yet.

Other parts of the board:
MH1, MH2, MH3, MH4: MountingHole_3.2mm

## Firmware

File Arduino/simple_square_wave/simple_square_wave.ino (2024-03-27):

//
// simple example from the MCP DAC library online
// https://github.com/michd/Arduino-MCP492X
//

#include "MCP_DAC.h" // Include the library

#define PIN_SPI_CHIP_SELECT_DAC 6 // Or any pin you'd like to use
#define PIN_LDAC 7 // nLDAC needs to be set low

#define WAVE_AMP 100

MCP4921 myDac;

void setup() {
  // put your setup code here, to run once:
  pinMode( PIN_LDAC, OUTPUT);
  digitalWrite( PIN_LDAC, LOW);   // MCP4921 datasheet says this may be tied low
  SPI.begin();
  myDac.begin( PIN_SPI_CHIP_SELECT_DAC);
}

void loop() {
  // put your main code here, to run repeatedly:

  // generate a small square wave about the mid-range
  myDac.fastWriteA(2048 + WAVE_AMP);
  delay(10);  // 10ms delay so 1/20ms (50Hz)
  myDac.fastWriteA(2048 - WAVE_AMP);
  delay(10);
}

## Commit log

2024-02-05 copy over multi-channel and initial sine wave design
    [42TU_transformer.scad, A11AB.stp, EC12 Encoder 10mm 3pin.stp, LCD_16x2_sparkfun.scad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]
2024-02-20 Add files via upload
    This is the design we have for now, we will run the simulations now and tweak the values accordingly.
    [sine-output.kicad_sch]
2024-02-21 Add files via upload
    Arduino Shield for Sine-Output TENS
    [InTENSArduinoSheild.kicad_pcb, InTENSArduinoSheild.kicad_sch]
2024-02-21 Add files via upload
    InTENS Arduino Shield Folder
    [InTENSArduinoSheild.kicad_pcb, InTENSArduinoSheild.kicad_sch]
2024-02-21 Attempt to restore project
    [PCB.kicad_pcb, PCB.kicad_sch]
2024-02-22 Serious edits during 2/22 meeting by Eric
    [PCB.kicad_pcb, PCB.kicad_sch]
2024-02-25 fixed scematic wiring, PCB tracks, checked footprint dimensions, and added 3D models
    [PCB.kicad_pcb, PCB.kicad_sch]
2024-03-04 Updated PCB (correct orientation)
    [Arduino-UNO.stp, PCB.kicad_pcb]
2024-03-04 semi-updated from Eric 3/4 notes
    [PCB.drl, PCB.kicad_pcb, PCB.kicad_sch]
2024-03-04 updated PCB from 3/4 Eric Meeting
    [PCB.kicad_pcb, PCB.kicad_sch]
2024-03-05 ERIC: Add part numbers to symbols for ordering
    [PCB.kicad_sch]
2024-03-05 ERIC: generate V1 gerbers with GND fixed
    [PCB-B_Cu.gbr, PCB-B_Mask.gbr, PCB-B_Silkscreen.gbr, PCB-Edge_Cuts.gbr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]
2024-03-05 Eric's version of layout
    [PCB-B_Cu.gbr, PCB-B_Mask.gbr, PCB-B_Silkscreen.gbr, PCB-Edge_Cuts.gbr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]
2024-03-27 Create ArduinoCode
    code for InTENS Device
2024-03-27 Add (working) Arduino example code
2024-03-28 Add files via upload
    PCB Board for battery
    [BatteryPCB.kicad_pcb, BatteryPCB.kicad_sch]
2024-03-29 Updates from 3/29 comments
    [BatteryPCB.kicad_pcb, BatteryPCB.kicad_sch]
2024-03-30 In progress changes from 3/29 2nd comments
    [BatteryPCB.kicad_sch, my_battery.kicad_pcb, my_battery.kicad_sch]
2024-03-30 2nd Update from 3/29 comments
    [BatteryPCB.kicad_pcb, BatteryPCB.kicad_sch]
2024-03-30 2nd Updates from 3/29 Comments
    [BatteryPCB.kicad_pcb]
2024-03-31 Updated from 3/30 comments
    [BatteryPCB.kicad_pcb, BatteryPCB.kicad_sch]
2024-03-31 Update README.md
    3/30 Eric notes for 2/29 updated Battery PCB
2024-04-01 4/1 trim pot change
    [BatteryPCB.kicad_pcb, BatteryPCB.kicad_sch]
2024-04-01 4/1 trim pot change + gerber files
    [BatteryPCB-B_Cu.gbr, BatteryPCB-B_Mask.gbr, BatteryPCB-B_Silkscreen.gbr, BatteryPCB-Edge_Cuts.gbr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]
2024-05-16 Add files via upload
    Electrode + housing CAD designs
    [halfclamplargedistance.STL, layer.stl, makercase.stl]

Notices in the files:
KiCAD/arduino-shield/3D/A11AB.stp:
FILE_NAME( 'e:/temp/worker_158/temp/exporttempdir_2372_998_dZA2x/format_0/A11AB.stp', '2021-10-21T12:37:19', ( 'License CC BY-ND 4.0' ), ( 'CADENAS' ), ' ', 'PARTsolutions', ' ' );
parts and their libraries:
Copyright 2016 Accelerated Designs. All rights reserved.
